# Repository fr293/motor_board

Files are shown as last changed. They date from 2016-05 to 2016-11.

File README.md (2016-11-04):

# stepper motor control board

This motor control board is designed to work with the [Open Flexure microscope](https://github.com/rwb27/openflexure_microscope) and connect to a Raspberry Pi.  It is based around three parallel ATTiny 841 microcontrollers running the Arduino Firmware through SpenceKonde's [ATTinyCore](https://github.com/SpenceKonde/ATTinyCore). 

Each ATTiny 841 controls a ULN2003 Darlington transistor array operating at 5V, running a 28BYJ-48 stepper motor with a 64:1 gear ratio.

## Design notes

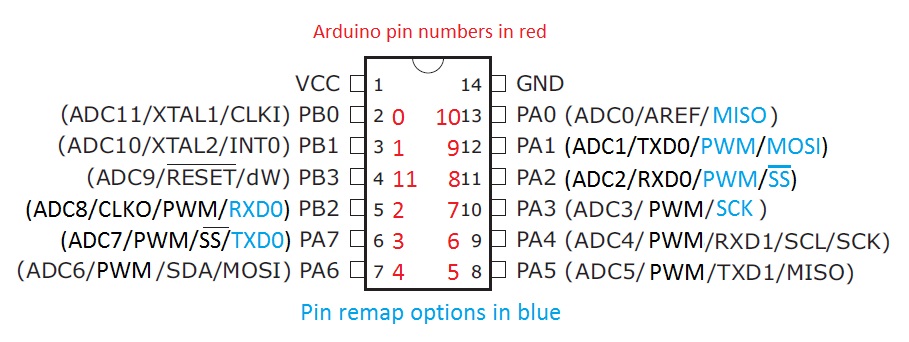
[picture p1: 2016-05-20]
tiny841_pinout.jpeg

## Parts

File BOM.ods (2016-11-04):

Bill of Materials for
Notes | Part name | part quantity | Schematic Part names | Value | Device | Package | Eagle Library | Digikey part # | other supplier link | Price
 | PCA9306 I2C bus voltage translator | 1 | U1 |  | PCA9306D I2C bus voltage translator | SOIC-8 | i2c | 568-4215-1-ND
 | PTC Resettable Fuses | 1 | F1 | .12A 30V PPTC. Hold Current: 0.12A, Trip Current: 0.39A, Maximum voltage: 48VDC, Current Rating 10A | TE Connectivity PolySwitch nanoASMDC Resettable Fuse parts # F63422-000, and RF1343-000 | 1206 (3216 metric) | Sparkfun-PowerIC | NANOASMDC012F-2CT-ND
 | LM340MP | 4 | IC1, IC2, IC3, IC4 | 5V | Sourced as LM340MP [LM340S on design] | SOT223 | linear | LM340MP-5.0/NOPBCT-ND
 | AT TINY 841 | 3 | IC5, IC6, IC7 |  | AT TINY 441/841-SSU | SOIC14N | bt_avr | ATTINY441-SSU-ND | ATTINY841-SSURDKR-ND
 | ULN 2003 | 3 | IC8, IC9, IC10 | 50v Max, 500mA | ULN 2003 AD | SO16 | uln-adn | 296-1368-5-ND
 | BSS138 Transistor | 1 | Q1 | 200mA/50V | N-CHANNEL MOSFET BSS138 | SO23-3 | SparkFun-DiscreteSemi | BSS138CT-ND
 | SPI programmer plug | 3 | ISP-X, ISP-Y, ISP-Z |  | AVR_SPI_PRG_60FFSET_PADS | 2x3_offset | SparkFun-Connectors | 952-2121-ND
 | barrel connector 5.5x2.1mm | 1 | J1 | positive to tip | 5.5mm OD x 2.1mm ID barrel power connector (industry standard mating diameter) |  | SparkFun-Connectors |  | https://www.sparkfun.com/products/12748
 | 5-pin molex connector series 87438 | 3 | MOTOR-X, MOTOR-Y, MOTOR-Z |  | 87438-0543 Molex connector |  | Con-molex | WM7649CT-ND
 | 4-pin molex connector series 87438 | 3 | OUT-A, OUT-B, Input |  | 87438-0443 Molex connector |  | Con-molex | WM7648CT-ND
 | 2200Ω Resistor | 5 | R1, R2, R4, R5, R15 | 2200Ω 1/8W, 0.1% | 2200Ω Resistor | M0805 | resistor | P2.2KDACT-ND
 | 220KΩ Resistor | 1 | R3 | 220KΩ, 1/8W, 1% | 220KΩ Resistor | M0805 | resistor | P220KCCT-ND
 | 4700Ω Resistor | 3 | R6, R7, R8 | 4700Ω, 1/8W, 1% | 4700Ω Resistor | M0805 | resistor | P4.70KCCT-ND
 | 150Ω Resistor | 6 | R9, R10, R11, R12, R13, R14 | 150Ω, 1/8W, 1% | 150Ω Resistor | M0805 | resistor | P150CCT-ND
 | 2MΩ Resistor | 1 | R16 | 2MΩ, 1/8W, 1% | 2MΩ Resistor | M0805 | resistor | P2.00MCCT-ND
 | 0.22uF Capacitor | 4 | C1, C3, C4, C5 | 0.22uF, 50V, 10% | capacitor | 0805 | Sparkfun-capacitors | 1276-6478-1-ND
100nF cap in C9-11 is same as 0.1uF cap in C6-9 | 0.1uF Capacitor | 7 | C2, C6, C7, C8, C9, C10, C11 | 0.1uF, 50V, 10% | capacitor | 0805 | Sparkfun-capacitors | 478-1395-1-ND | http://www.mouser.com/ProductDetail/AVX/08055F104KAT2A/?qs=ZiTRcRMDrL8Tl%252bt5AACK1Q%3D%3D
 | Red LED SMT | 3 | LED1, LED3, LED5 | red, Vf 2.5V, forward current 25ma | 0805 red LED | 0805 | led | 475-1278-1-ND
 | Green LED SMT | 3 | LED2, LED4, LED6 | green, Vf 2V, forward current 20ma | 0805 green LED | 0805 | led | 350-2044-1-ND
 | Schottky Rectifier Diode | 1 | D1 | 1A/40V, min Forward voltage: 0.41V@1A | Bourns CD214A-B140LF | SMA-DIODE-KIT | SparkFun-DiscreteSemi | CD214A-B140LFCT-ND

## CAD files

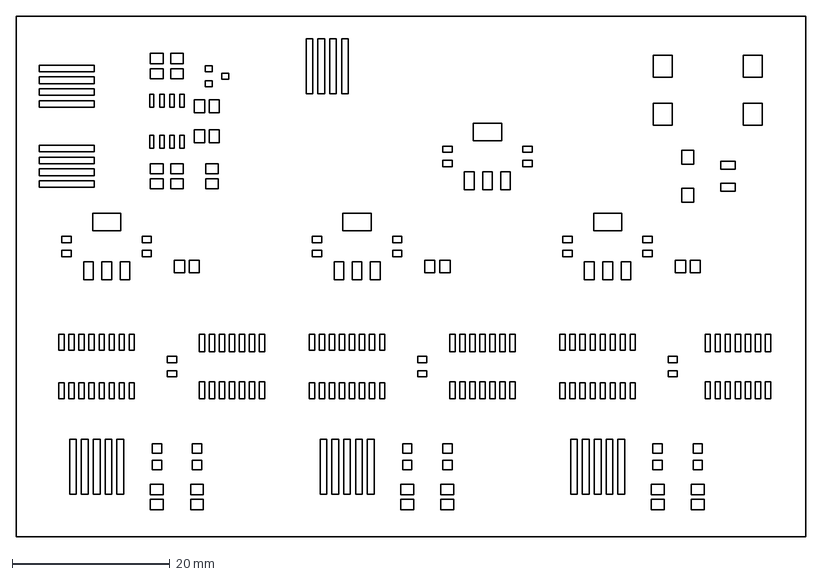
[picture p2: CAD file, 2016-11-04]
schematicmrpRevF_stencil.dxf
100.0 x 66.0 mm

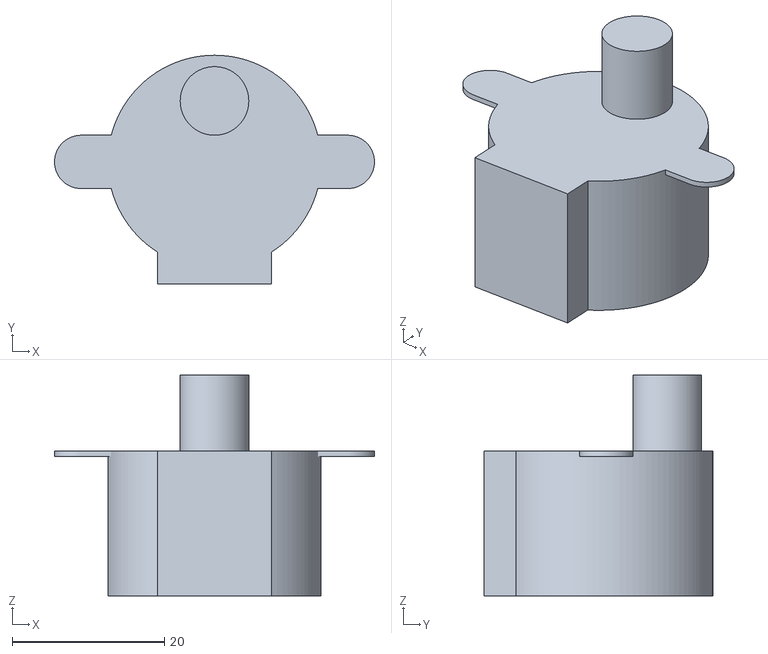
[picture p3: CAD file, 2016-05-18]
motor_bound.stl
42.0 x 30.0 x 29.0

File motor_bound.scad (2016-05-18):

$fn = 100;

union(){
    cylinder(r=14,h=19);
    translate([0,8,19]) cylinder(r=4.5,h=10);
    hull(){
        translate([17.5,0,18.3]) cylinder(r=3.5,h=0.7);
        mirror([1,0,0]) translate([17.5,0,18.3]) cylinder(r=3.5,h=0.7);
          }
         translate([-7.5,-16,0]) cube([15,5,19]);
}

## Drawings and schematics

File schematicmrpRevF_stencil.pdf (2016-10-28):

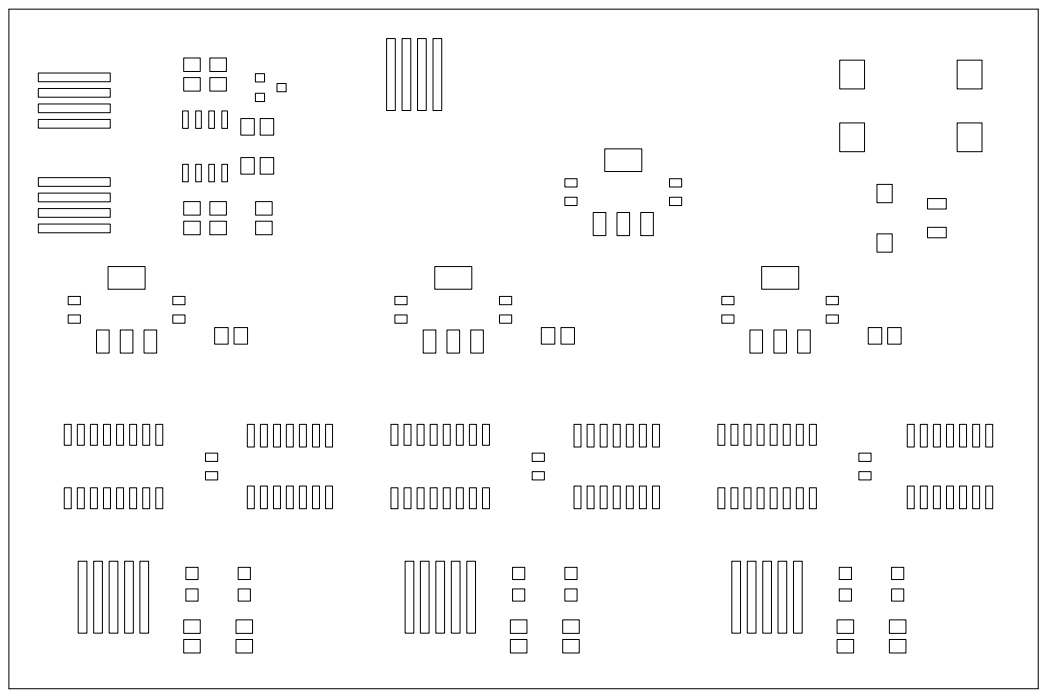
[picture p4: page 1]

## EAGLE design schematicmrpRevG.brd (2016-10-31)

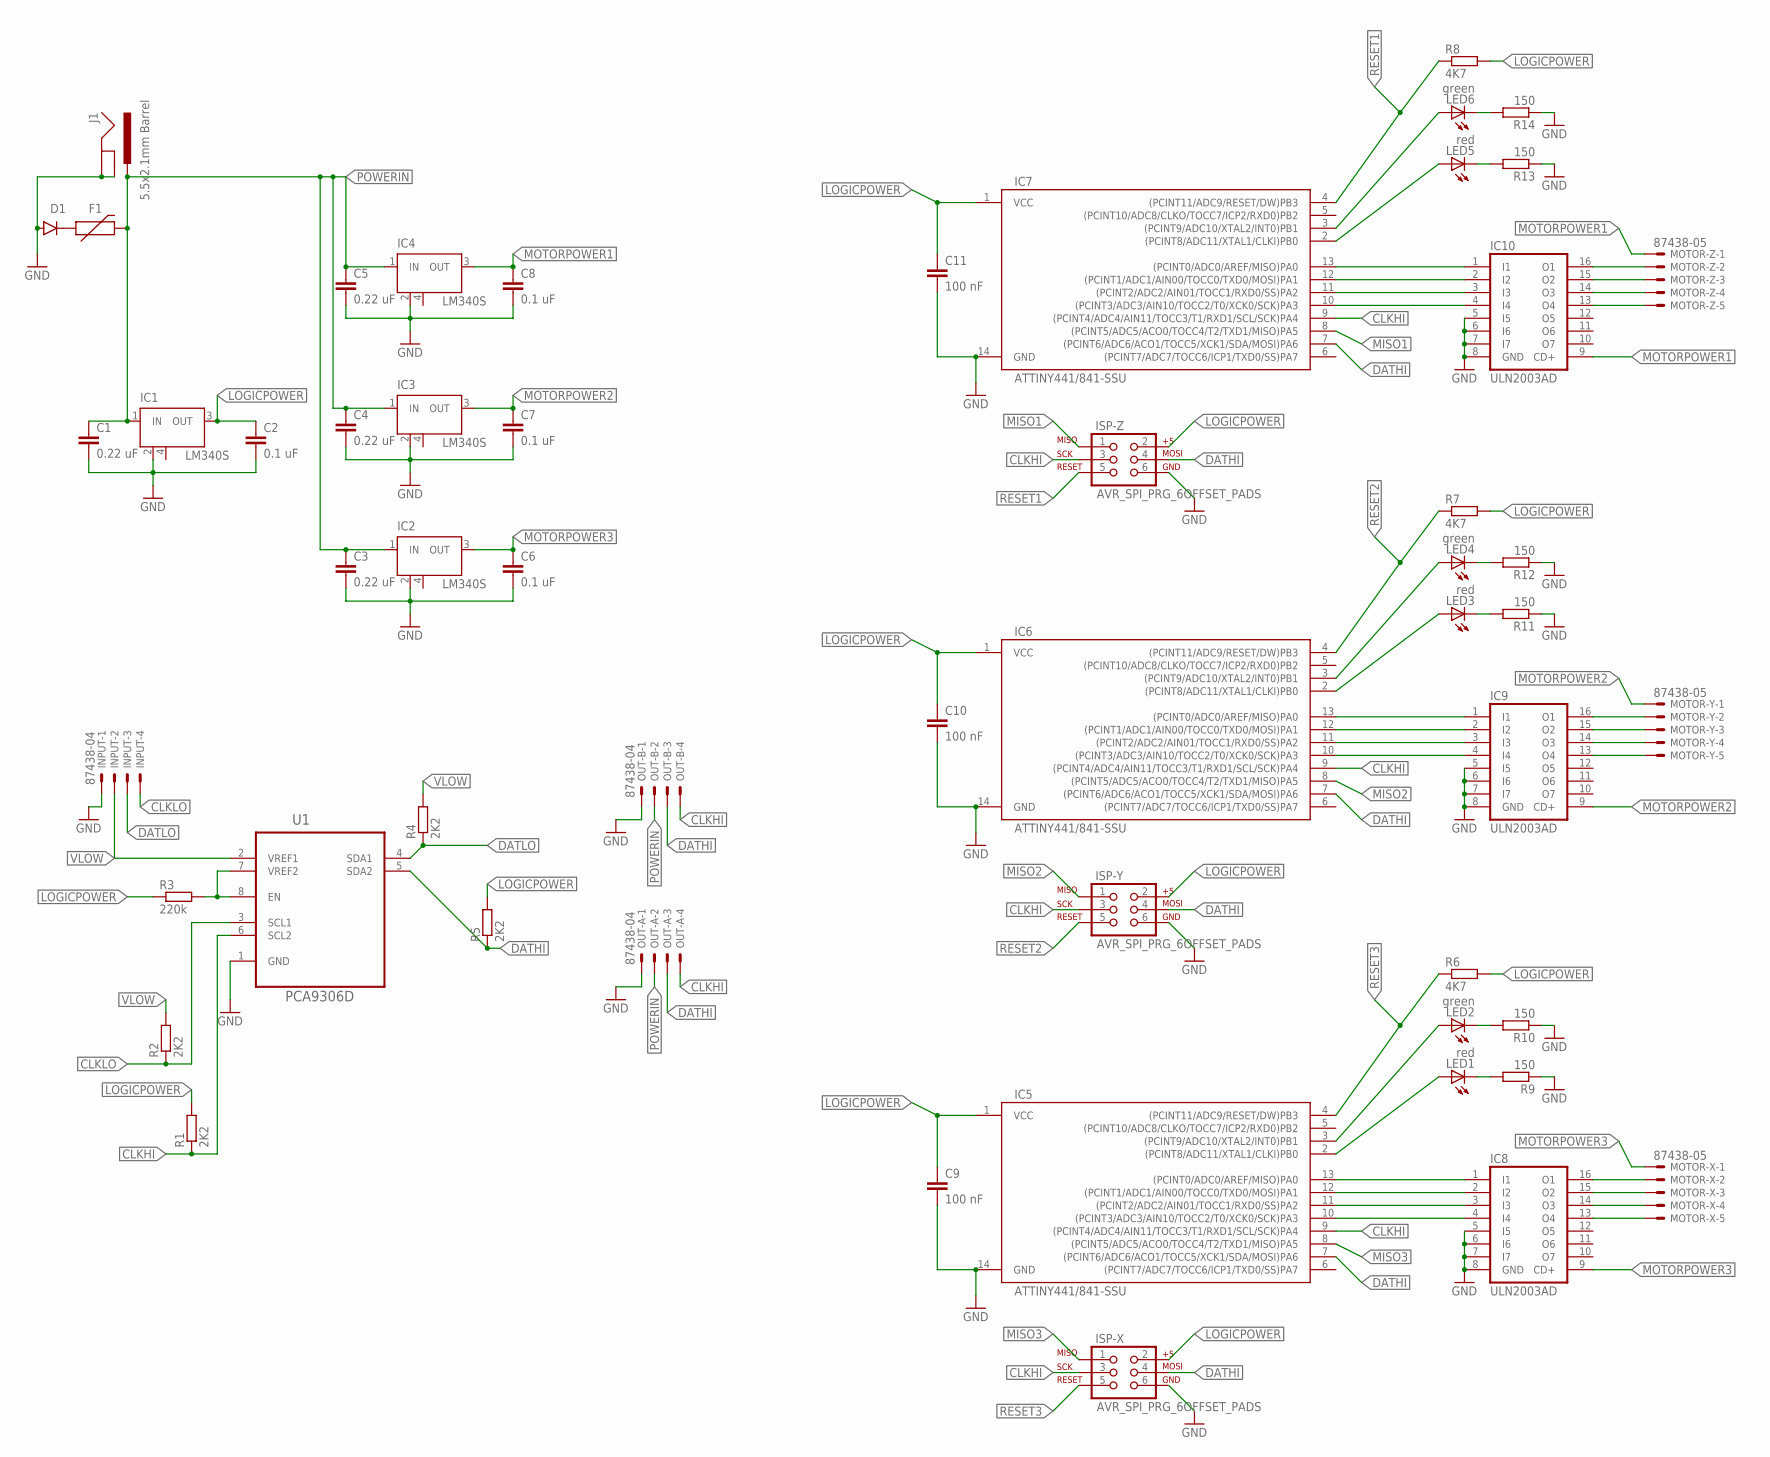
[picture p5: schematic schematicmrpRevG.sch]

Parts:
C1, C3, C4, C5: 0.22 uF; 0805; MPN 0805B224K500CT
C2, C6, C7, C8: 0.1 uF; 0805; MPN 08055C104KAT2A
C9, C10, C11: 100 nF; 0805; MPN 08055F104KAT2A
D1: 3A/600V; SMA-DIODE-KIT; MPN CD214A-B140LF
F1: PTCSMD; PTC-1206; MPN NANOSMDC012F-2
IC1, IC2, IC3, IC4: LM340S; SOT223; MPN LM340MP-5.0/NOPB
IC5, IC6, IC7: ATTINY441/841-SSU; SOIC14N; MPN ATTINY841-SSU
IC8, IC9, IC10: ULN2003AD; SO16; MPN ULN2003ADR
INPUT: 87438-04; MPN 87438-0443
ISP-X: AVR_SPI_PRG_6OFFSET_PADS; 2X3_OFFSET; MPN BG050-06A-0-0450-0737-0350-L-D
ISP-Y: AVR_SPI_PRG_6OFFSET_PADS; 2X3_OFFSET; MPN BG050-06A-0-0450-0737-0350-L-D
ISP-Z: AVR_SPI_PRG_6OFFSET_PADS; 2X3_OFFSET; MPN BG050-06A-0-0450-0737-0350-L-D
J1: 5.5x2.1mm Barrel; POWER_JACK_SMD; MPN FC68148S
LED1, LED3, LED5: red; CHIPLED_0805; MPN LSR976
LED2, LED4, LED6: green; CHIPLED_0805; MPN 5988170107F
MOTOR-X: 87438-05; MPN 87438-0543
MOTOR-Y: 87438-05; MPN 87438-0543
MOTOR-Z: 87438-05; MPN 87438-0543
OUT-A: 87438-04; MPN 87438-0443
OUT-B: 87438-04; MPN 87438-0443
R1, R2, R4, R5: 2K2; M0805; MPN ERA6AEB222V
R3: 220k; M0805; MPN WCR0805-220KFI
R6, R7, R8: 4K7; M0805; MPN WCR0805-4K7FI
R9, R10, R11, R12, R13, R14: 150; M0805; MPN WCR0805-150RFI
U1: PCA9306D; SOIC127P600X175-8N; MPN PCA9306D

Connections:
CLKHI: IC5.9 ((PCINT4/ADC4/AIN11/TOCC3/T1/RXD1/SCL/SC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), IC6.9 ((PCINT4/ADC4/AIN11/TOCC3/T1/RXD1/SCL/SC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), IC7.9 ((PCINT4/ADC4/AIN11/TOCC3/T1/RXD1/SCL/SC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), ISP-X.3, ISP-Y.3, ISP-Z.3, OUT-A.4, OUT-B.4, R1.1, U1.6 (SCL2)
CLKLO: INPUT.4, R2.1, U1.3 (SCL1)
DATHI: IC5.7 ((PCINT6/ADC6/ACO1/TOCC5/XCK1/SDA/MOSI)P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), IC6.7 ((PCINT6/ADC6/ACO1/TOCC5/XCK1/SDA/MOSI)P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), IC7.7 ((PCINT6/ADC6/ACO1/TOCC5/XCK1/SDA/MOSI)P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), ISP-X.4, ISP-Y.4, ISP-Z.4, OUT-A.3, OUT-B.3, R5.1, U1.5 (SDA2)
DATLO: INPUT.3, R4.1, U1.4 (SDA1)
GND: C1.2, C2.2, C3.2, C4.2, C5.2, C6.2, C7.2, C8.2, C9.2, C10.2, C11.2, D1.A, IC1.2 (GND), IC1.4 (GND), IC2.2 (GND), IC2.4 (GND), IC3.2 (GND), IC3.4 (GND), IC4.2 (GND), IC4.4 (GND), IC5.14 (GND), IC6.14 (GND), IC7.14 (GND), IC8.5 (I5), IC8.6 (I6), IC8.7 (I7), IC8.8 (GND), IC9.5 (I5), IC9.6 (I6), IC9.7 (I7), IC9.8 (GND), IC10.5 (I5), IC10.6 (I6), IC10.7 (I7), IC10.8 (GND), INPUT.1, ISP-X.6, ISP-Y.6, ISP-Z.6, J1.GND (GNDBREAK), J1.P$4 (GND), OUT-A.1, OUT-B.1, R9.1, R10.1, R11.1, R12.1, R13.1, R14.1, U1.1 (GND)
LOGICPOWER: C2.1, C9.1, C10.1, C11.1, IC1.3 (OUT), IC5.1 (VCC), IC6.1 (VCC), IC7.1 (VCC), ISP-X.2, ISP-Y.2, ISP-Z.2, R1.2, R3.1, R5.2, R6.2, R7.2, R8.2
MISO1: IC7.8 ((PCINT5/ADC5/ACO0/TOCC4/T2/TXD1/MISO)PA5), ISP-Z.1
MISO2: IC6.8 ((PCINT5/ADC5/ACO0/TOCC4/T2/TXD1/MISO)PA5), ISP-Y.1
MISO3: IC5.8 ((PCINT5/ADC5/ACO0/TOCC4/T2/TXD1/MISO)PA5), ISP-X.1
MOTORPOWER1: C8.1, IC4.3 (OUT), IC10.9 (CD+), MOTOR-Z.1
MOTORPOWER2: C7.1, IC3.3 (OUT), IC9.9 (CD+), MOTOR-Y.1
MOTORPOWER3: C6.1, IC2.3 (OUT), IC8.9 (CD+), MOTOR-X.1
unnamed: LED4.C, R12.2
unnamed: LED3.C, R11.2
unnamed: R3.2, U1.7 (VREF2), U1.8 (EN)
unnamed: IC10.16 (O1), MOTOR-Z.2
unnamed: IC10.15 (O2), MOTOR-Z.3
unnamed: LED6.C, R14.2
unnamed: LED5.C, R13.2
unnamed: IC10.14 (O3), MOTOR-Z.4
unnamed: IC10.13 (O4), MOTOR-Z.5
unnamed: IC7.13 ((PCINT0/ADC0/AREF/MISO)PA0), IC10.1 (I1)
unnamed: IC7.12 ((PCINT1/ADC1/AIN00/TOCC0/TXD0/MOSI)PA1), IC10.2 (I2)
unnamed: IC7.11 ((PCINT2/ADC2/AIN01/TOCC1/RXD0/SS)PA2), IC10.3 (I3)
unnamed: IC7.10 ((PCINT3/ADC3/AIN10/TOCC2/T0/XCK0/SCK)PA3), IC10.4 (I4)
unnamed: IC7.3 ((PCINT9/ADC10/XTAL2/INT0)PB1), LED6.A
unnamed: IC7.2 ((PCINT8/ADC11/XTAL1/CLKI)PB0), LED5.A
unnamed: IC9.16 (O1), MOTOR-Y.2
unnamed: IC9.15 (O2), MOTOR-Y.3
unnamed: IC9.14 (O3), MOTOR-Y.4
unnamed: IC9.13 (O4), MOTOR-Y.5
unnamed: IC6.13 ((PCINT0/ADC0/AREF/MISO)PA0), IC9.1 (I1)
unnamed: IC6.12 ((PCINT1/ADC1/AIN00/TOCC0/TXD0/MOSI)PA1), IC9.2 (I2)
unnamed: IC6.11 ((PCINT2/ADC2/AIN01/TOCC1/RXD0/SS)PA2), IC9.3 (I3)
unnamed: IC6.10 ((PCINT3/ADC3/AIN10/TOCC2/T0/XCK0/SCK)PA3), IC9.4 (I4)
unnamed: IC6.3 ((PCINT9/ADC10/XTAL2/INT0)PB1), LED4.A
unnamed: IC6.2 ((PCINT8/ADC11/XTAL1/CLKI)PB0), LED3.A
unnamed: LED2.C, R10.2
unnamed: LED1.C, R9.2
unnamed: IC8.16 (O1), MOTOR-X.2
unnamed: IC8.15 (O2), MOTOR-X.3
unnamed: IC8.14 (O3), MOTOR-X.4
unnamed: IC8.13 (O4), MOTOR-X.5
unnamed: IC5.13 ((PCINT0/ADC0/AREF/MISO)PA0), IC8.1 (I1)
unnamed: IC5.12 ((PCINT1/ADC1/AIN00/TOCC0/TXD0/MOSI)PA1), IC8.2 (I2)
unnamed: IC5.11 ((PCINT2/ADC2/AIN01/TOCC1/RXD0/SS)PA2), IC8.3 (I3)
unnamed: IC5.10 ((PCINT3/ADC3/AIN10/TOCC2/T0/XCK0/SCK)PA3), IC8.4 (I4)
unnamed: IC5.3 ((PCINT9/ADC10/XTAL2/INT0)PB1), LED2.A
unnamed: IC5.2 ((PCINT8/ADC11/XTAL1/CLKI)PB0), LED1.A
unnamed: D1.C, F1.1
POWERIN: C1.1, C3.1, C4.1, C5.1, F1.2, IC1.1 (IN), IC2.1 (IN), IC3.1 (IN), IC4.1 (IN), J1.VIN0 (PWR), OUT-A.2, OUT-B.2
RESET1: IC7.4 ((PCINT11/ADC9/RESET/DW)PB3), ISP-Z.5, R8.1
RESET2: IC6.4 ((PCINT11/ADC9/RESET/DW)PB3), ISP-Y.5, R7.1
RESET3: IC5.4 ((PCINT11/ADC9/RESET/DW)PB3), ISP-X.5, R6.1
VLOW: INPUT.2, R2.2, R4.2, U1.2 (VREF1)

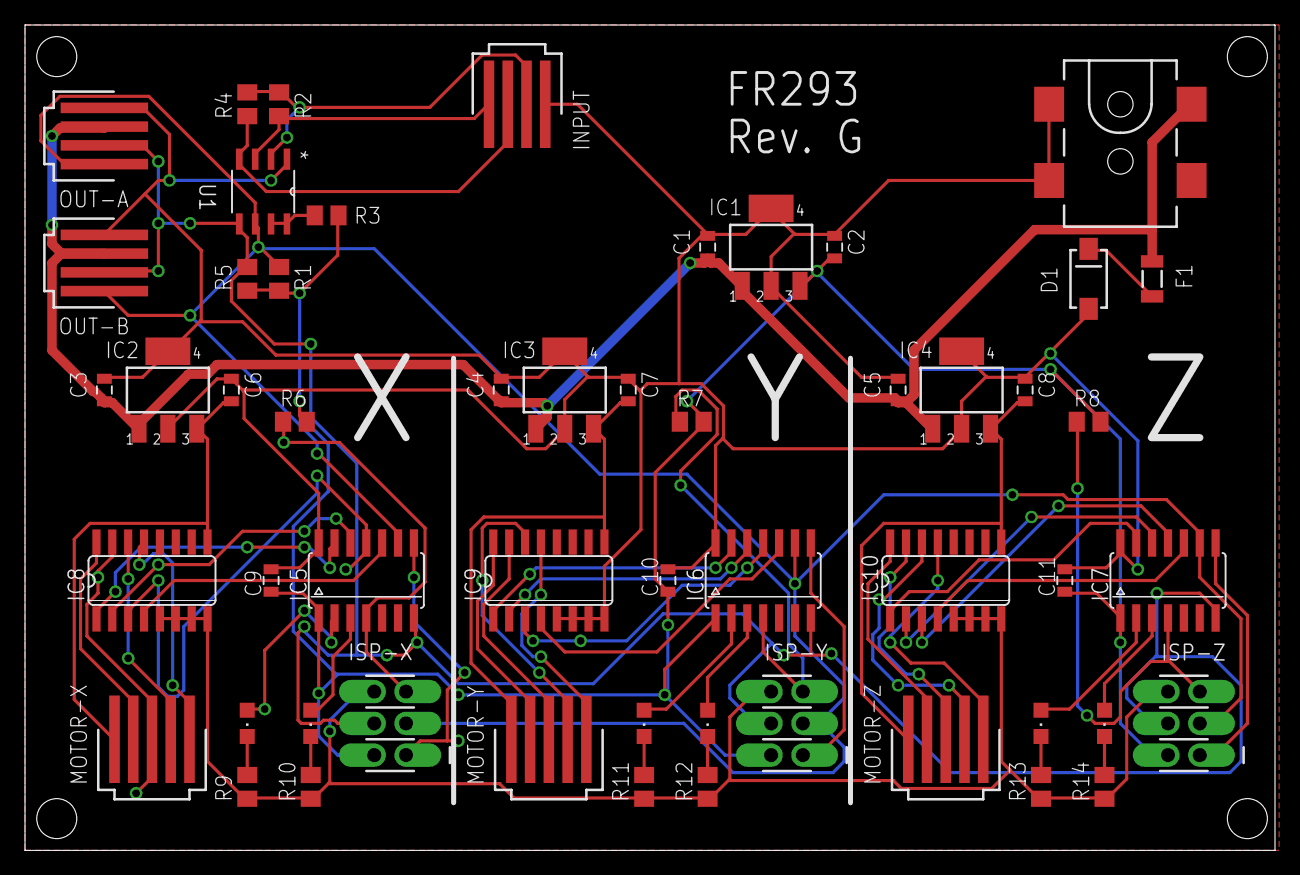
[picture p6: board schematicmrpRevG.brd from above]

Board: 2 copper layers, 100.0 x 66.0 mm, 54 parts (0 on the bottom side), 55 nets.

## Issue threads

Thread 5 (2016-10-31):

### ISSUE TITLE
Arduino Firmware for ATTiny841, Spence Konde's ATTinyCore?

### ISSUE THREAD

**Issue by mathewlippincott** [fr293/motor_board#5]
Is this the firmware being used for the ATTiny841?
https://github.com/SpenceKonde/ATTinyCore

**Comment by fr293** [comment]
That’s the one. It seems to be pretty active at the moment, which is good!

Yours truly,

Fergus Riche 
Magdalene College
Cambridge
Mobile: +447974304049

**Comment by mathewlippincott** [comment]
Cool, added info to the readme and made a pull request!

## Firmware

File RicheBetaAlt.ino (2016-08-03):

///////Beta version of motor controller code, released 09/04/16/////////
///////Author: Fergus Riche, fr293@cam.ac.uk////////////////////////////

// QueueArray creates a FIFO queue, StepperF is my modified version of the 
//bundled stepper library that deals with half stepping and turns off all 
//phases when motor is not moving to save power, WireS is the i2c library 
//for the attiny 841

#include <QueueArray.h> //http://playground.arduino.cc/Code/QueueArray
#include <StepperF_alt.h>   
#include <WireS.h>    //https://github.com/orangkucing/WireS             

// led is an indicator led attached to physical pin 2 of the attiny 841 SOIC
//define your own slave address for each motor axis with I2C_SLAVE_ADDR
//the motor has 2048 full steps per revolution; i.e. 4096 half steps
#define led                1
#define act                0
#define I2C_SLAVE_ADDR     48
#define STEPS           4096 

// create a queue of ints to act as the command buffer 
// create a stepper attached to physical pins 10, 11, 12, 13
QueueArray <int> buffer;
Stepper stepper(STEPS, 7, 8, 9, 10);

//create variables for the current task, and for any values recieved over
//i2c
int currenttask = 0;
int receivedValue = 0;


// enable the led as an output, blink it at startup to show that everything
//is ok
//begin the i2c communication and define the action to be performed on
// reciept of data as an interupt routine
//set the speed of the stepper in rpm
void setup()
{
  pinMode(led,OUTPUT);
  pinMode(act,OUTPUT);             
  Blink(led);
  Wire.begin(I2C_SLAVE_ADDR);     
  Wire.onReceive(transfer);
  stepper.setSpeed(1);
}


// the loop runs ad infinitum and checks the status of the buffer
//if it contains commands, take the first one out of the queue and make it
//the current task for the stepper and turn the activity light on
//if not, just turn the activity light off

void loop()
{
  
if (!buffer.isEmpty()) 
  {
  currenttask = buffer.dequeue();

  digitalWrite(act,HIGH);
  stepper.step(currenttask);
  
  }
  
 else
  {
    digitalWrite(act,LOW);
  }

 }
  

// this function is called as an interrupt on reciept of a correct address
//byte on the i2c line
// bytes arriving in twos are converted into signed 16 bit ints and added
//to the queue, the check is there to prevent misalignment of bytes as a 
//result of a misread
void transfer(size_t c)
{   
  if (Wire.available() == 2)
  {
  int receivedValue = Wire.read() << 8 | Wire.read();
  buffer.enqueue(receivedValue); 
  }
}


// this function is there to make blinking a pin easier for debug purposes
//it contains delays, and cannot be used inside any other interrupts
void Blink(int pin)
{ 
  for(int i = 0; i <3; i++){
    digitalWrite(pin,HIGH);
    delay (100);
    digitalWrite(pin,LOW);
    delay (100);
  }
}

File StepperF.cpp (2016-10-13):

/*
 *§§§§§§§§§§§§§§§§§§§§§§§§§§§§§§§§§§§§§§§§§§§§§§§§§§§§§§§§§§§§§§§§§§§§§
 *Fergus Riche's Updated Stepper Library
 *This library can drive four wire unipolar motors in half stepping mode.
 *It was written to drive 28BYJ-48 – 5V Stepper Motors.
 *
 *§§§§§§§§§§§§§§§§§§§§§§§§§§§§§§§§§§§§§§§§§§§§§§§§§§§§§§§§§§§§§§§§§§§§§
 *
 *
 * Stepper.cpp - Stepper library for Wiring/Arduino - Version 1.1.0
 *
 * Original library        (0.1)   by Tom Igoe.
 * Two-wire modifications  (0.2)   by Sebastian Gassner
 * Combination version     (0.3)   by Tom Igoe and David Mellis
 * Bug fix for four-wire   (0.4)   by Tom Igoe, bug fix from Noah Shibley
 * High-speed stepping mod         by Eugene Kozlenko
 * Timer rollover fix              by Eugene Kozlenko
 * Five phase five wire    (1.1.0) by Ryan Orendorff
 *
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
 *
 * Drives a unipolar, bipolar, or five phase stepper motor.
 *
 * When wiring multiple stepper motors to a microcontroller, you quickly run
 * out of output pins, with each motor requiring 4 connections.
 *
 * By making use of the fact that at any time two of the four motor coils are
 * the inverse of the other two, the number of control connections can be
 * reduced from 4 to 2 for the unipolar and bipolar motors.
 *
 * A slightly modified circuit around a Darlington transistor array or an
 * L293 H-bridge connects to only 2 microcontroler pins, inverts the signals
 * received, and delivers the 4 (2 plus 2 inverted ones) output signals
 * required for driving a stepper motor. Similarly the Arduino motor shields
 * 2 direction pins may be used.
 *
 * The sequence of control signals for 5 phase, 5 control wires is as follows:
 *
 * Step C0 C1 C2 C3 C4
 *    1  0  1  1  0  1
 *    2  0  1  0  0  1
 *    3  0  1  0  1  1
 *    4  0  1  0  1  0
 *    5  1  1  0  1  0
 *    6  1  0  0  1  0
 *    7  1  0  1  1  0
 *    8  1  0  1  0  0
 *    9  1  0  1  0  1
 *   10  0  0  1  0  1
 *
 * The sequence of control signals for 4 control wires is as follows:
 *
 * Step C0 C1 C2 C3
 *    1  1  0  1  0
 *    2  0  1  1  0
 *    3  0  1  0  1
 *    4  1  0  0  1
 *
 * The sequence of controls signals for 2 control wires is as follows
 * (columns C1 and C2 from above):
 *
 * Step C0 C1
 *    1  0  1
 *    2  1  1
 *    3  1  0
 *    4  0  0
 *
 * The circuits can be found at
 *
 * http://www.arduino.cc/en/Tutorial/Stepper
 */

#include "Arduino.h"
#include "StepperF.h"

///*
// * two-wire constructor.
// * Sets which wires should control the motor.
// */
//Stepper::Stepper(int number_of_steps, int motor_pin_1, int motor_pin_2)
//{
//  this->step_number = 0;    // which step the motor is on
//  this->direction = 0;      // motor direction
//  this->last_step_time = 0; // time stamp in us of the last step taken
//  this->number_of_steps = number_of_steps; // total number of steps for this motor
//
//  // Arduino pins for the motor control connection:
//  this->motor_pin_1 = motor_pin_1;
//  this->motor_pin_2 = motor_pin_2;
//
//  // setup the pins on the microcontroller:
//  pinMode(this->motor_pin_1, OUTPUT);
//  pinMode(this->motor_pin_2, OUTPUT);
//
//  // When there are only 2 pins, set the others to 0:
//  this->motor_pin_3 = 0;
//  this->motor_pin_4 = 0;
//  this->motor_pin_5 = 0;
//
//  // pin_count is used by the stepMotor() method:
//  this->pin_count = 2;
//}


/*
 *   constructor for four-pin version
 *   Sets which wires should control the motor.
 */
Stepper::Stepper(int number_of_steps, int motor_pin_1, int motor_pin_2,
                                      int motor_pin_3, int motor_pin_4)
{
  this->step_number = 0;    // which step the motor is on
  this->direction = 0;      // motor direction
  this->last_step_time = 0; // time stamp in us of the last step taken
  this->number_of_steps = number_of_steps; // total number of steps for this motor

  // Arduino pins for the motor control connection:
  this->motor_pin_1 = motor_pin_1;
  this->motor_pin_2 = motor_pin_2;
  this->motor_pin_3 = motor_pin_3;
  this->motor_pin_4 = motor_pin_4;

  // setup the pins on the microcontroller:
  pinMode(this->motor_pin_1, OUTPUT);
  pinMode(this->motor_pin_2, OUTPUT);
  pinMode(this->motor_pin_3, OUTPUT);
  pinMode(this->motor_pin_4, OUTPUT);

  // When there are 4 pins, set the others to 0:
  this->motor_pin_5 = 0;

  // pin_count is used by the stepMotor() method:
  this->pin_count = 4;
}

///*
// *   constructor for five phase motor with five wires
// *   Sets which wires should control the motor.
// */
//Stepper::Stepper(int number_of_steps, int motor_pin_1, int motor_pin_2,
//                                      int motor_pin_3, int motor_pin_4,
//                                      int motor_pin_5)
//{
//  this->step_number = 0;    // which step the motor is on
//  this->direction = 0;      // motor direction
//  this->last_step_time = 0; // time stamp in us of the last step taken
//  this->number_of_steps = number_of_steps; // total number of steps for this motor
//
//  // Arduino pins for the motor control connection:
//  this->motor_pin_1 = motor_pin_1;
//  this->motor_pin_2 = motor_pin_2;
//  this->motor_pin_3 = motor_pin_3;
//  this->motor_pin_4 = motor_pin_4;
//  this->motor_pin_5 = motor_pin_5;
//
//  // setup the pins on the microcontroller:
//  pinMode(this->motor_pin_1, OUTPUT);
//  pinMode(this->motor_pin_2, OUTPUT);
//  pinMode(this->motor_pin_3, OUTPUT);
//  pinMode(this->motor_pin_4, OUTPUT);
//  pinMode(this->motor_pin_5, OUTPUT);
//
//  // pin_count is used by the stepMotor() method:
//  this->pin_count = 5;
//}
//
/*
 * Sets the speed in revs per minute
 */
void Stepper::setSpeed(long whatSpeed)
{
  this->step_delay = 60L * 1000L * 1000L / this->number_of_steps / whatSpeed;
}

/*
 * Moves the motor steps_to_move steps.  If the number is negative,
 * the motor moves in the reverse direction.
 */
void Stepper::step(int steps_to_move)
{
  int steps_left = abs(steps_to_move);  // how many steps to take

  // determine direction based on whether steps_to_mode is + or -:
  if (steps_to_move > 0) { this->direction = 1; }
  if (steps_to_move < 0) { this->direction = 0; }


  // decrement the number of steps, moving one step each time:
  while (steps_left > 0)
  {
    unsigned long now = micros();
    // move only if the appropriate delay has passed:
    if (now - this->last_step_time >= this->step_delay)
    {
      // get the timeStamp of when you stepped:
      this->last_step_time = now;
      // increment or decrement the step number,
      // depending on direction:
      if (this->direction == 1)
      {
        this->step_number++;
        if (this->step_number == this->number_of_steps) {
          this->step_number = 0;
        }
      }
      else
      {
        if (this->step_number == 0) {
          this->step_number = this->number_of_steps;
        }
        this->step_number--;
      }
      // decrement the steps left:
      steps_left--;
      // step the motor to step number 0, 1, ..., {3 or 10}
//      if (this->pin_count == 5)
//        stepMotor(this->step_number % 10);
//      else
        stepMotor(this->step_number % 8);
    }
  }
   stepMotor(8); 
}

/*
 * Moves the motor forward or backwards.
 */
void Stepper::stepMotor(int thisStep)
{
//  if (this->pin_count == 2) {
//    switch (thisStep) {
//      case 0:  // 01
//        digitalWrite(motor_pin_1, LOW);
//        digitalWrite(motor_pin_2, HIGH);
//      break;
//      case 1:  // 11
//        digitalWrite(motor_pin_1, HIGH);
//        digitalWrite(motor_pin_2, HIGH);
//      break;
//      case 2:  // 10
//        digitalWrite(motor_pin_1, HIGH);
//        digitalWrite(motor_pin_2, LOW);
//      break;
//      case 3:  // 00
//        digitalWrite(motor_pin_1, LOW);
//        digitalWrite(motor_pin_2, LOW);
//      break;
//    }
//  }
//  if (this->pin_count == 4) {
    switch (thisStep) {
      case 0:  // 1000
        digitalWrite(motor_pin_1, HIGH);
        digitalWrite(motor_pin_2, LOW);
        digitalWrite(motor_pin_3, LOW);
        digitalWrite(motor_pin_4, LOW);
      break;
      case 1:  // 1100
        digitalWrite(motor_pin_1, HIGH);
        digitalWrite(motor_pin_2, HIGH);
        digitalWrite(motor_pin_3, LOW);
        digitalWrite(motor_pin_4, LOW);
      break;
      case 2:  //0100
        digitalWrite(motor_pin_1, LOW);
        digitalWrite(motor_pin_2, HIGH);
        digitalWrite(motor_pin_3, LOW);
        digitalWrite(motor_pin_4, LOW);
      break;
      case 3:  //0110
        digitalWrite(motor_pin_1, LOW);
        digitalWrite(motor_pin_2, HIGH);
        digitalWrite(motor_pin_3, HIGH);
        digitalWrite(motor_pin_4, LOW);
      break;
      case 4:  // 0010
        digitalWrite(motor_pin_1, LOW);
        digitalWrite(motor_pin_2, LOW);
        digitalWrite(motor_pin_3, HIGH);
        digitalWrite(motor_pin_4, LOW);
      break;
      case 5:  // 0011
        digitalWrite(motor_pin_1, LOW);
        digitalWrite(motor_pin_2, LOW);
        digitalWrite(motor_pin_3, HIGH);
        digitalWrite(motor_pin_4, HIGH);
      break;
      case 6:  //0001
        digitalWrite(motor_pin_1, LOW);
        digitalWrite(motor_pin_2, LOW);
        digitalWrite(motor_pin_3, LOW);
        digitalWrite(motor_pin_4, HIGH);
        break;
      case 7:  //1001
        digitalWrite(motor_pin_1, HIGH);
        digitalWrite(motor_pin_2, LOW);
        digitalWrite(motor_pin_3, LOW);
        digitalWrite(motor_pin_4, HIGH);
        break;
      case 8:  //0000
        digitalWrite(motor_pin_1, LOW);
        digitalWrite(motor_pin_2, LOW);
        digitalWrite(motor_pin_3, LOW);
        digitalWrite(motor_pin_4, LOW);
        break;

            

    }
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

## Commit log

2016-05-18 Add files via upload
    This model is a reasonably accurate upper bound on the 28BYJ-48 – 5V Stepper Motor
    [motor_bound.scad, motor_bound.stl]
2016-10-18 Added bill of materials
    I went through the eagle files and made a bill of materials in an ODF
    spreadsheet. It has generic part specifications, footprints, and part
    numbers for the Digikey catalog.
    [RevF_BOM.ods]
2016-10-18 updated BOM
    resolved notes, updated parts quantities, confirmed ATTiny 841
    [BOM.ods]
2016-10-27 SMT stencils
    added board stencils for surface mount solder application
2016-11-02 added stencil DXF, fixed BSS138 digikey part X in BOM
    [BOM.ods, schematicmrpRevF_stencil.dxf]

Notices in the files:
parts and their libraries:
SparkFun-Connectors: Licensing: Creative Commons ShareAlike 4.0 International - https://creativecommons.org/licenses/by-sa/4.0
